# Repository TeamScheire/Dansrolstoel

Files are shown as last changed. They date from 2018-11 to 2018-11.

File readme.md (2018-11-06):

# Dansrolstoel voor Pluim

Kim wil terug dansen met Pluim, maar Pluim zit in een rolstoel en heeft beperkte kracht in zijn lichaam. Hij wil zelf met deze beperkte kracht toch de leiding kunnen nemen en zo terug kunnen dansen met zijn vrouw.

Hardware en software voor de arduino nano in de dansrolstoel van Pluim - ontworpen, geschreven en gemaakt door Ronald Van Ham.

Zie [Team Scheire op canvas.be](https://www.canvas.be/team-scheire/pluim-wil-dansen) voor info en beeldmateriaal.

De oplossing bestaat uit 3 delen:

- motoren op de wielen (onder de zit of achteraan)
- een module onder de voeten. 
- aansturing via een Arduino en h-bruggen

De batterij kan op 1 van deze plaatsen zitten.

## Motoren 
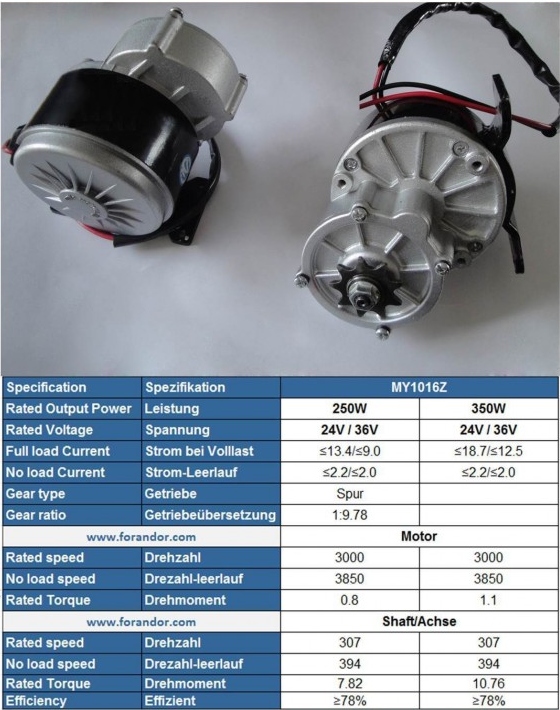
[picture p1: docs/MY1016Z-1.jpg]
MY1016Z


Ze moeten genoeg koppel kunnen leveren. Door de ingebouwde tandwielen is dit mogelijk.

Te verkrijgen via [ali express](https://www.aliexpress.com/w/my1016z-12v.html) of [forandor](https://forandor.com/index.php?route=product/product&path=68&product_id=324)

## Voetbesturing
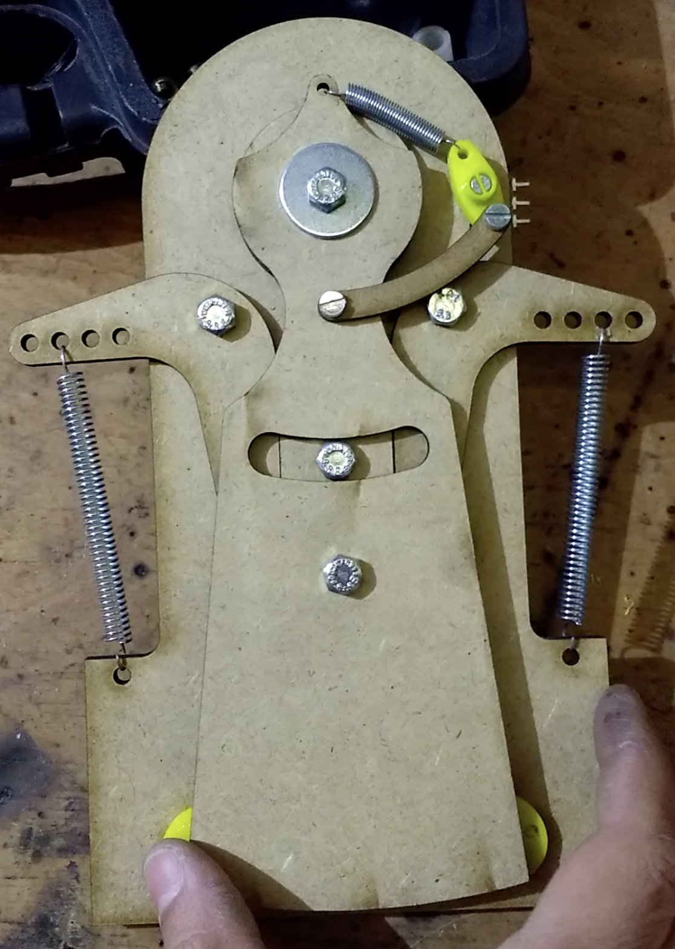
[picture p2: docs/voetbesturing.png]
Voetbesturing

Het belangrijkste onderdeel is de op maat gemaakte voetbesturing. Pluim kan zijn voeten nog wel rond hun as draaien. 

De voetbesturing leest deze draaibeweging uit, met zo weinig mogelijk weerstand, zodat Pluim zo weinig mogelijk kracht moet zetten.

Voetbesturing gemonteerd

Op iedere voetbesturing zitten twee kogellagers om de bewegingen met zo weinig mogelijk wrijving te laten gebeuren.
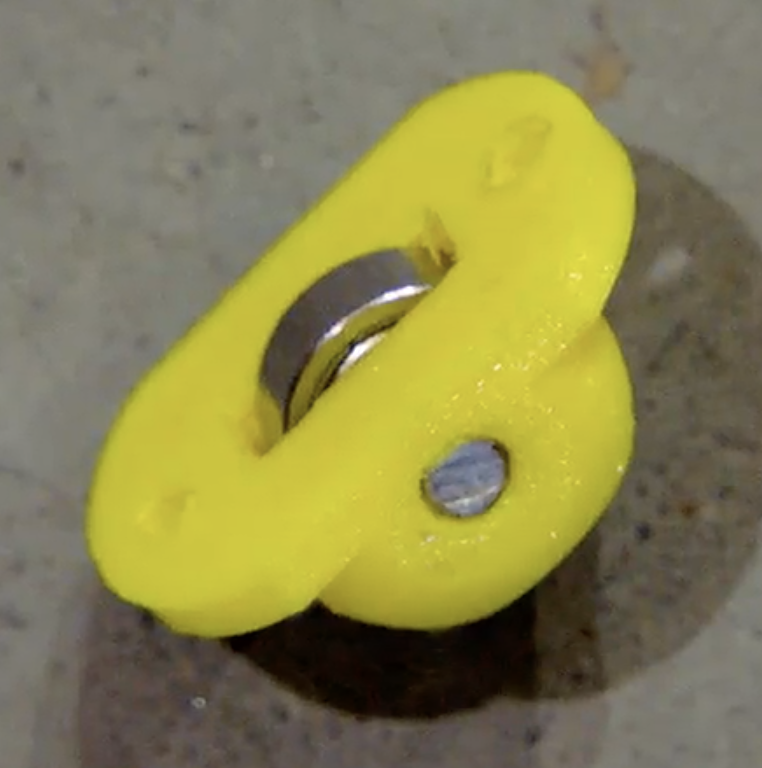
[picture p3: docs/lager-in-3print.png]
kogellager in 3D print

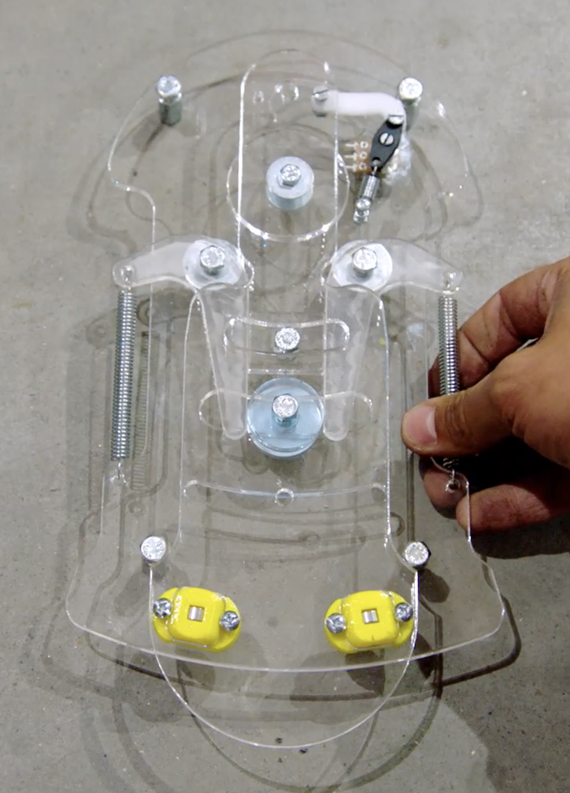
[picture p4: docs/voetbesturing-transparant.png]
Transparante voetbesturing


In deze voetbesturing zit een potentiometer langs de onderkant die de draaiing uitmeet.

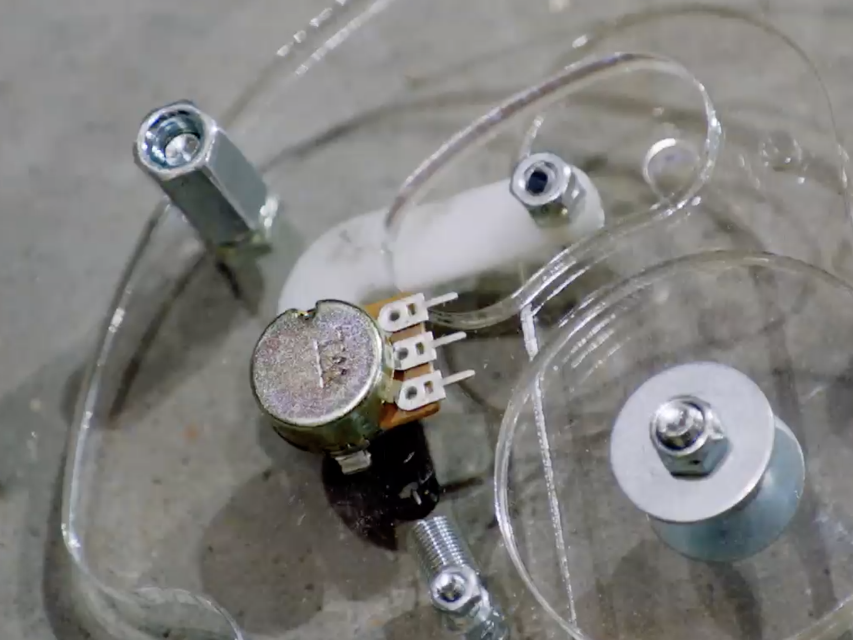
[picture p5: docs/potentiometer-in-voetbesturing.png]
Potentiometer


## Controller

### Arduino nano
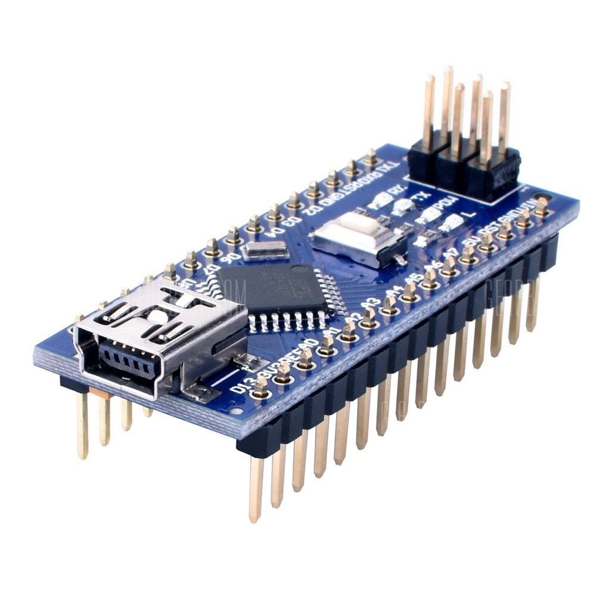
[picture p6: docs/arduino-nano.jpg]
Arduino Nano


Het hart van de controle gebeurt via een Arduino nano, de kleinere versie van de arduino. Op zich kan het uiteraard ook met een gewone Arduino, maar deze nano is kleiner en kwa rekenkracht goed genoeg voor wat nodig is.

De Arduino leest de signalen van de potentiometers in de voetbesturingen uit en zet ze om in signalen voor de twee h-bruggen. Voor elke motor één.

Een Arduino nano is overal te verkrijgen [officiële van Arduino](https://store.arduino.cc/usa/arduino-nano) maar via China zijn er goedkopere varianten te vinden ;).

### BTS7960 H-brug motor driver
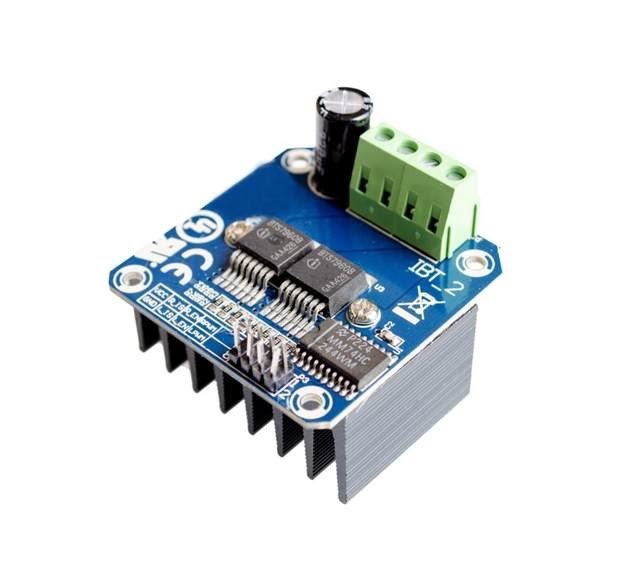
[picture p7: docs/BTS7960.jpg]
BTS7960 H-Brug motor driver


Elke motor heeft zijn BTS7960 H-Brug motor driver en deze verwerkt de signalen van de arduino en zet ze om in de juiste stroompulsen voor de motoren.

Een uitleg hoe je met deze H-Brug kan werken staat [op deze instructable](https://www.instructables.com/id/Motor-Driver-BTS7960-43A/) en de specificaties vind je [in deze bijlage](docs/bts7960b-datasheet.pdf).

DE BTS7960 H-Brug motor driver is te verkrijgen via [ali express](https://www.aliexpress.com/w/wholesale-BTS7960.html)

### Connecties
- A0: Batterijspanning via spanningsdeler, om de batterijspanning te controlleren, gekleurde led aan te sturen en indien nodig stoppen om batterij te beschermen. De weerstanden dienen gekozen te worden zodat de spanning nooit (ook niet tijdens het opladen) boven de 5 volt aan de ingang komt. Nadien via voltmeter en serial monitor calibratiefactor bepalen
- A6: Potentiometer onder rechtervoet 
- A7: Potentiometer onder linkervoet 

Deze 2 dienen in software aangepast te worden door te kijken via seriele monitor welke waarde de middenpositie heeft, en wat de 2 uiterste zijn)
Deze waarden vul je in bij RMin, RMid, RMax en LMin, LMid, LMax. Dit dient normaal maar 1 keer te gebeuren, maar soms even checken is niet slecht 

PIN 3, 9, 10, 11 PWM outputs, die gekoppeld zijn aan timer 1 en 2. Dus dan blijft Timer 0 beschikbaar als watchdog timer. We kunnen ook de frequentie van Timer 1 en 2 aanpassen zodat de motoren minder lawaai maken. Let op, de H-Brug moet deze hogere frequentie aankunnen.

Pin 6, 7, 8: GRB LED

## Assemblage

Een controlepaneel achteraan de rolstoel combineert de h-bruggen, de Arduino, de voetbesturing en verdeelt de stroom. Een 12v batterij levert de stroom. Alles mooi weggewerkt achter een beschermkap.

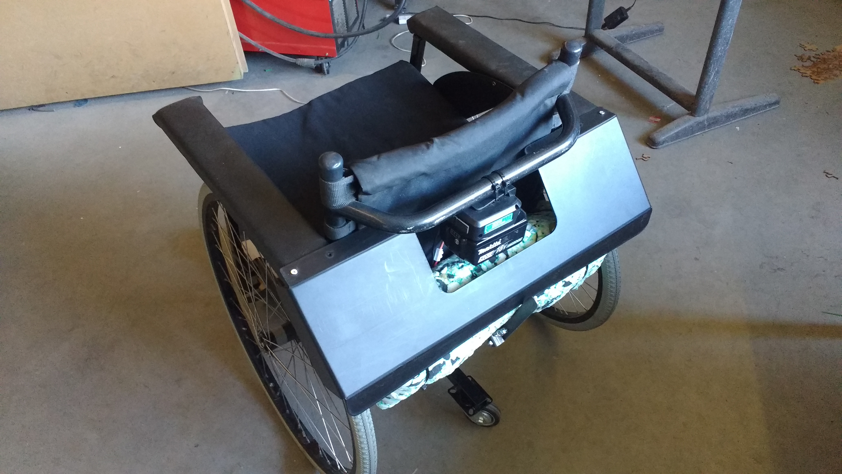
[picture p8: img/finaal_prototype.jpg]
Afgewerkt prototype


Met een heel mooi resultaat: twee mensen die hun passie terug hebben gevonden: samen kunnen dansen.

Kim en Pluim

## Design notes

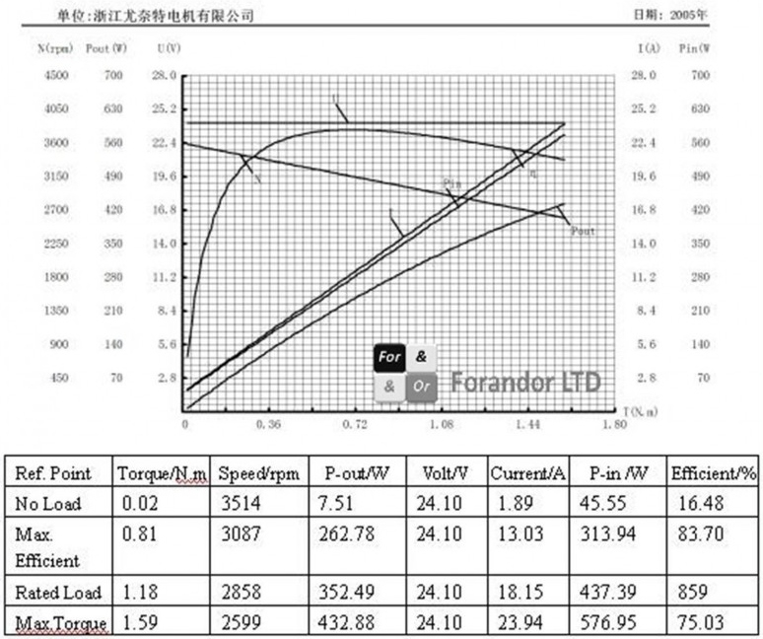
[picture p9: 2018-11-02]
docs/MY1016Z-3.jpg

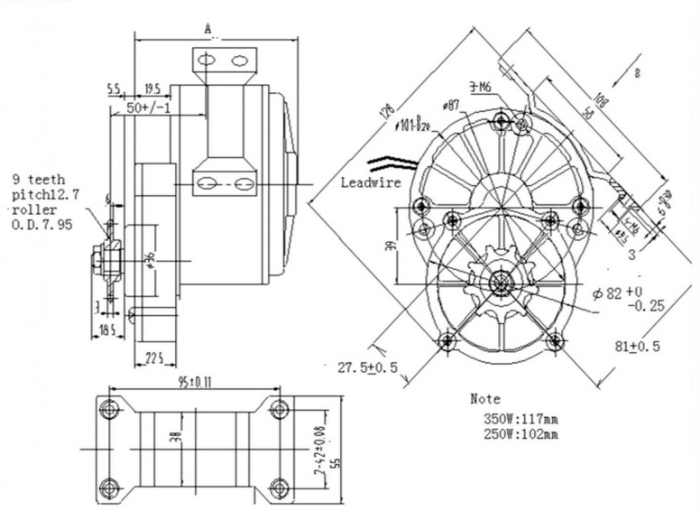
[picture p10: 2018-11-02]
docs/MY1016Z-2.jpg

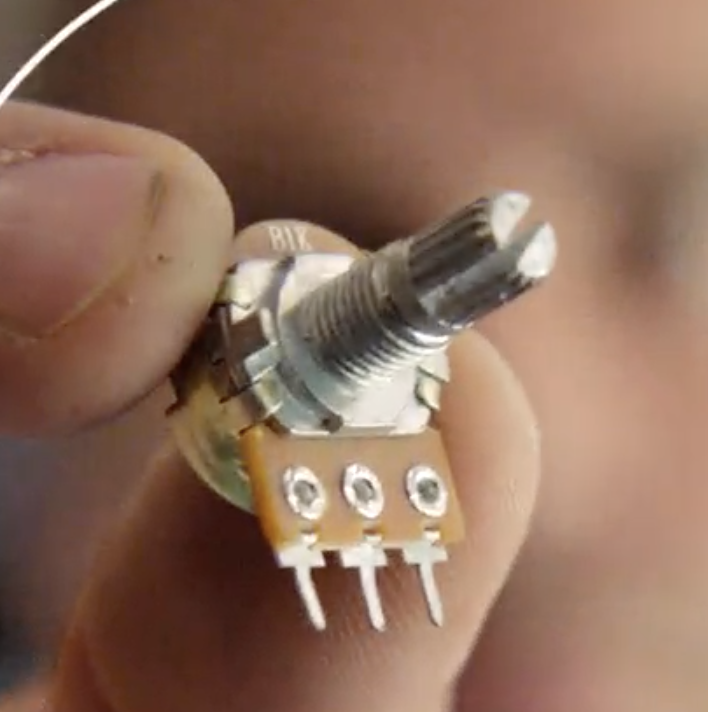
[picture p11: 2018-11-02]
docs/potentiometer.png

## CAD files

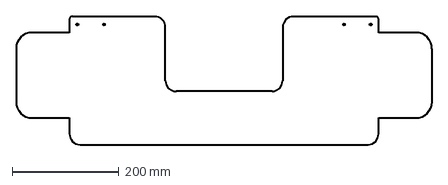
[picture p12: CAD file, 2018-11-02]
designs/Afschermkap.dxf
780.0 x 240.0 mm

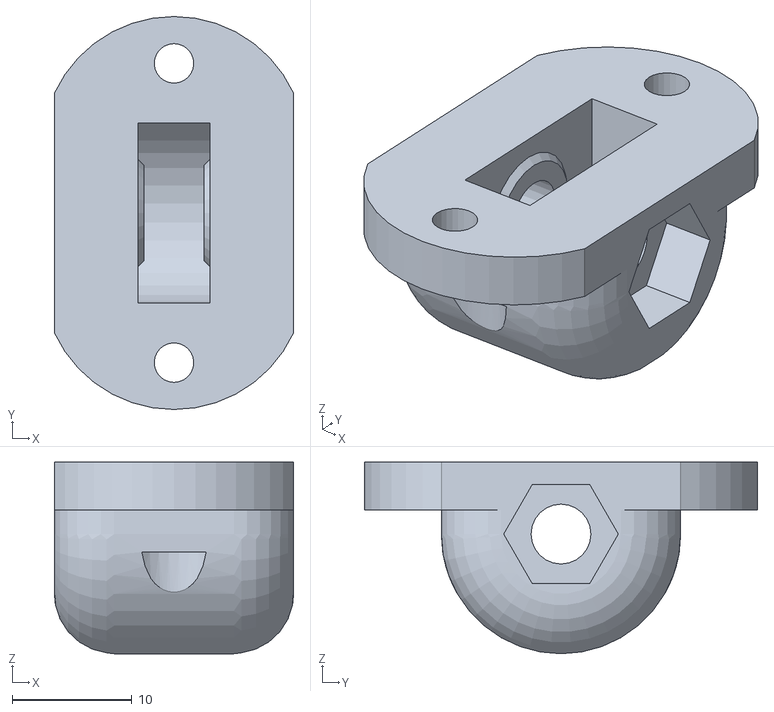
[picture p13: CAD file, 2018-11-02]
designs/WielMetLager5-14-5Closed.stl
20.0 x 32.8 x 16.0

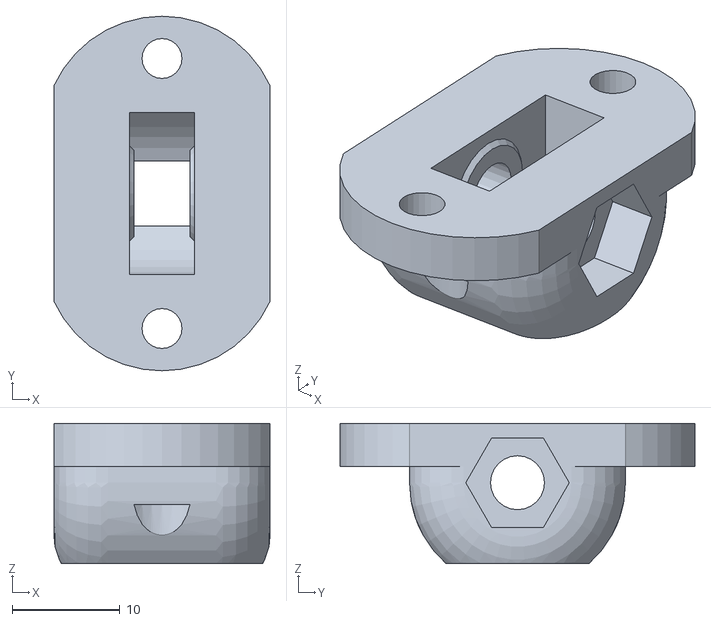
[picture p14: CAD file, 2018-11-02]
designs/WielMetLager5-14-5Open.stl
20.0 x 32.8 x 13.0

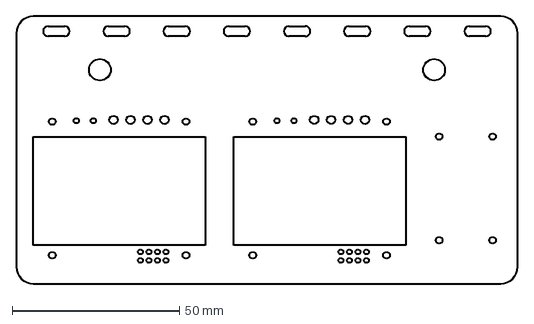
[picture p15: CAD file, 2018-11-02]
designs/BaseplatePluim.dxf
150.0 x 80.0 mm

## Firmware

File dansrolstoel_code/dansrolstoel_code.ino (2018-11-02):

/* Software voor de arduino nano in de dansrolstoel van Pluim - geschreven door Ronald Van Ham

connecties:
A0: Batterijspanning via spanningsdeler, om de batterijspanning te controlleren, gekleurde led aan te sturen en indien nodig stoppen om batterij te beschermen
De weerstanden dienen gekozen te worden dat de spanning nooit (ook niet tijdens het opladen) boven de 5 volt aan de ingang komt. 
Nadien via voltmeter en serial monitor calibratiefactor bepalen
A6: Potenriometer onder rechtervoet 
A7: Potenriometer onder linkervoet 
Deze 2 dienen in software aangepast te worden door te kijken via seriele monitor welke waarde de middenpositie heeft, en wat de 2 uiterste zijn)
Deze waarden vul je in bij RMin, RMid, RMax en LMin, LMid, LMax. Dit dient normaal maar 1 keer te gebeuren, maar soms even checken is niet slecht 

PIN 3,9,10,11 PWM outputs, die gekoppeld zijn aan timer 1 en 2. Dus dan blijft Timer 0 beschikbaar als watchdog timer
We kunnen ook de frequentie van Timer 1 en 2 aanpassen zodat de motoren minder lawaai maken. Let op, de H-Brug moet deze hogere frequentie aankunnen.

Pin 6,7,8: GRB LED
*/


#include <avr/interrupt.h>   // we gaan timer0 interrupt als watchdog timer gerbuiken, omdat de watchdogtimer in de chinese arduino nano niet werkt. 
                              // Andere oplossing is om andere bootloader in de Chinese Arduino Nano te steken

// De gebruikte variabelen:
int PotR = 0;        // Waarde van de rechter potentiometer
int PotL = 0;        // vaarde van de liknker potentiometer
float ControlR = 0;         //  Stuursignaal rechtse motor
float ControlRFilter = 0;   //  Gefilterde waaarde, om schokken te vermijden en iets rustiger op te trekken. 
float ControlL = 0;  
float ControlLFilter = 0;
int Marge = 6;              // Marge vanaf wanneer de motoren iets mogen doen, = dode band in het midden
int Voltage = 0;            // gemeten spanning x10
float FilterConst = 0.2;    //  Filterconstante hangt af van hoe precies Pluim zijn voeten kan controleren

int PWMout1L = 0;           // Waardes output PWM (analog out)
int PWMout2L = 0; 
int PWMout1R = 0;        
int PWMout2R = 0; 

const int RMin = 130;        // instelwaardes van de hoeken van de voetpotentiometers. Af te lezen via SerialMonitor
const int RMid = 423;
const int RMax = 663;

const int LMin = 175;
const int LMid = 448;
const int LMax = 692;

void setup() {
  //Starten serial communications op 115200 bps:  Als commentaar in gewone werking, opzetten indien je hoeken wil instellen
  //Serial.begin(115200);
  //Serial.println("rolstoel Pluim");
  TCCR1B = TCCR1B & 0b11111000 | 0x01;   // Frequenties PWM aanpassen om de motoren stiller te maken. Maak hier commentaar van als de Hbrug niet snel genoeg is.
  TCCR2B = TCCR2B & 0b11111000 | 0x01;    // De werking blijft hetzelde, maar met iets meer lawaai van de motoren. Als het niet werkt, eerst beide lijnen commentaar maken
  pinMode(6, OUTPUT);                   // Deze 3 outputs dienen voor RGB led als batterij indicator. Zou ook via neopixel led kunnen
  pinMode(7, OUTPUT);
  pinMode(8, OUTPUT);
  
  ControlRFilter = 127;        // 0-126 is de ene richting, 127 stilstand, 128-255 is de andere richting
  ControlLFilter = 127;        // Dus bij opstart zetten we beide motoren af

  //Setup Timer0 to fire every 16ms as watchdog timer, zie internet: Er is blijkbaar een probleem met de bootloader in Chinese Arduino nano bij gebruikt watchdog timer 
  TCCR0B = 0x00;        //Disbale Timer2 while we set it up
  TCNT0  = 130;         //Reset Timer Count to 130 out of 255
  TIFR0  = 0x00;        //Timer2 INT Flag Reg: Clear Timer Overflow Flag
  TIMSK0 = 0x01;        //Timer2 INT Reg: Timer2 Overflow Interrupt Enable
  TCCR0A = 0x00;        //Timer2 Control Reg A: Wave Gen Mode normal
  TCCR0B = 0x07;        //Timer2 Control Reg B: Timer Prescaler set to 1024
}

void loop() {
  TCNT0 = 130;  // reset onze eigen watchdog timer0
 
  Voltage = map(10*analogRead(A0),0, 10240, 0, 214);   // Lees de batterijspanning en laat de kleur van de LED Rood of groen worden
  if (Voltage > 150) {
  digitalWrite(6, LOW);
  digitalWrite(7, HIGH); // Green
  digitalWrite(8, LOW);
  }
  else
  {
  digitalWrite(6, HIGH);  // Red
  digitalWrite(7, LOW);
  digitalWrite(8, LOW);
  }
  TCNT0 = 130;  // reset onze eigen watchdog timer0
  if (PWMout1L > 1 or PWMout1R > 1 or PWMout2L > 1 or PWMout2R > 1) {
  digitalWrite(8, HIGH);  //Blue     Laat de led blauw worden als de motoren aangestuurd worden, dan kunnen we de spanning van de batterij niet juist inschatten
  digitalWrite(7, LOW);
  }
  else {
  digitalWrite(8, LOW);   
  }
  
  PotR = analogRead(A6);  //  Lees beide voetsensoren in
  PotL = analogRead(A7);
  TCNT0 = 130;  // reset onze eigen watchdog timer0
  if(PotR < RMid)                                   // Doe een mapping voor de rechter motor, maar apart voor vooruit en achteruit. 
   {ControlR = map(PotR, RMin, RMid, 0, 127);
   if (PotR < RMin) {ControlR = 0;}
   }
  else
   {ControlR = map(PotR, RMid, RMax, 128, 255);
   if (PotR > RMax) {ControlR = 255;}
   } 
  if (ControlR < 0) {ControlR = 0;}        // limiteer de waarde
  if (ControlR > 255) {ControlR = 255;}

  if(PotL < LMid)                                // Doe een mapping voor de linker motor, maar apart voor vooruit en achteruit.
   {ControlL = map(PotL, LMin, LMid, 0, 127);
   if (PotL < LMin) {ControlL = 0;} 
   } 
  else
   {ControlL = map(PotL, LMid, LMax, 128, 255); 
   if (PotL > LMax) {ControlL = 255;}
   }
  if (ControlL < 0) {ControlL = 0;}     // limiteer ook deze waarde
  if (ControlL > 255) {ControlL = 255;}
  TCNT2 = 00;  // reset timer 2
  ControlRFilter = (FilterConst * ControlR + (1 - FilterConst) * ControlRFilter);  // Filteren omdat Pluim iets minder controle heeft. Dit is te tunen tot het goed voelt
  ControlLFilter = (FilterConst * ControlL + (1 - FilterConst) * ControlLFilter);
  
  //  Zet de motoren af, we gaan ze straks opzetten, maar alleen als de batterij voldoende vol is  
  PWMout1L = 1;        
  PWMout2L = 1;  

  PWMout1R = 1; 
  PWMout2R = 1;
  TCNT0 = 130;  // reset onze eigen watchdog timer0
  if(ControlLFilter > 127+Marge) {PWMout1L = 2*(ControlLFilter-128); PWMout2L = 1;  }  // MAp vooruit en achterui naar de juiste PWM pinnen
  if(ControlLFilter < 127-Marge) {PWMout1L = 1; PWMout2L = 2*(127-ControlLFilter);  }

  if(ControlRFilter > 127+Marge) {PWMout1R = 2*(ControlRFilter-128); PWMout2R = 1;  }  
  if(ControlRFilter < 127-Marge) {PWMout1R = 1; PWMout2R = 2*(127-ControlRFilter);  }
  TCNT0 = 130;  // reset onze eigen watchdog timer0

  if (Voltage > 135) {          // Als de batterij spanning voldoende hoog is, stuur de motoren aan
  analogWrite(3, PWMout1L);      // stuur de waardes effectief naar de H-Bruggen
  analogWrite(9, PWMout2L);  
  
  analogWrite(10, PWMout1R);
  analogWrite(11, PWMout2R);
  }
    TCNT2 = 00;  // reset timer 2
 
 
         //   Stuur alle gegevens naar het scherm, zet deze code actief om de potentiometers te calibreren en te debuggen
  /*
  Serial.println(Voltage);
  Serial.print("\t  ");

  Serial.print(PotL );
  Serial.print("\t  ");
  Serial.print(PotR );
  
  Serial.print("\t  ");
  TCNT2 = 00;  // reset timer 2
  Serial.print(ControlLFilter );
  Serial.print("\t  ");
  Serial.print(ControlRFilter );
  
  Serial.print("\t 1L ");
  Serial.print(PWMout1L );
  Serial.print("\t 2L ");
  Serial.print(PWMout2L );
  TCNT2 = 00;  // reset timer 2
  Serial.print("\t 1R ");
  Serial.print(PWMout1R );
  Serial.print("\t 2R ");
  Serial.print(PWMout2R );
  
  Serial.println( );
  */
}

//  De volgende code is de watchdog timer. Als de Arduino zou crashen, wordt de timer0 niet meer terug op 130 gezet en zal deze na enkele milliseconden op 255 staan 
//  en daarna een 'overflow interrupt' genereren. Dan gaan we gewoon onze arduino resetten. Dit gaat zo snel dat Pluim er zelfs niets van merkt.
//  Deze watchdog timer is niet strikt noodzakelijk, maar maakt het systeem wel betrouwbaarder.

void(* resetFunc) (void) = 0; //declare reset function @ address 0

ISR(TIMER0_OVF_vect) {   // Watchdog interrupt
  TIFR0 = 0x00;        //Timer2 INT Flag Reg: Clear Timer Overflow Flag
  resetFunc();         //call reset, reboot this controller
}

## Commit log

2018-11-02 versie met uitleg
    [Afschermkap.dxf, BaseplatePluim.dxf, VoetUnit.dxf, WielMetLager5-14-5Closed.stl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]
2018-11-03 Versie 2
    [VoetUnit - Copy.dxf]
2018-11-06 small corrections
    [VoetUnit - Copy.dxf]
